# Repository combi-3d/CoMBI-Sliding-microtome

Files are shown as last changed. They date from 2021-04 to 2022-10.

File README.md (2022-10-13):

# CoMBI-S (sliding microtome) 

1. STL file for making a white attachment of paraffin block by 3D printer (Fig. 4, designed by Josephine Galipon and Hiroyoshi Shirahata). Choose filament color as you need as a background color. In our report, we made attachments in white, and also add white crayon into paraffin, to get better contrast between specimen and background.

2. Arduino sketch for CoMBI-S low-cost system (Suppl. Fig. S2, written by Tohru Murakami)

3. SVG file of frost distributor (Suppl. Fig. S3, designed by Yuki Tajika)
   Acrylic plate with desirable thickness (2 mm) are processed by CO2 laser cutter. 1. Engrave black lines, 2. Cut red lines. Then,  3. Bend at black lines using bending heater. Adjust the bending angle according to the shape of each blade holder.

4. SVG file of molds for embedding with white-agarose (Suppl. Fig. S4, designed by Yuki Tajika)
   Acrylic plate with desirable thickness (2, 3, 5-mm) are processed by CO2 laser cutter. 1. Engrave magenta lines, 2. Cut blue lines, 3. Cut black lines.
   Set the radius of one part to 40mm, or the size of all 8 parts to 158 x 81 mm. Make a countersink at the bottom of "bottom plate".

These are supplemental data in: Scientific Reports 2021; 11: 13108.

Published online 2021 Jun 23. doi: 10.1038/s41598-021-92485-5 under the CC BY 4.0 licence.

(2021.3 submitted, 2021.4 in revision, 2021.6 accepted. Scientific Reports)

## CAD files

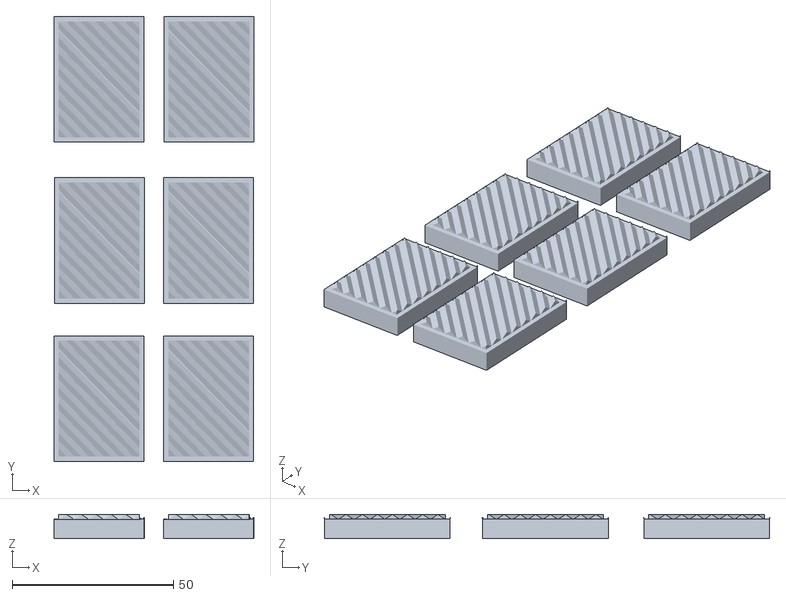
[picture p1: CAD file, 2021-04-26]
block 0001.stl
62.0 x 138.0 x 7.49

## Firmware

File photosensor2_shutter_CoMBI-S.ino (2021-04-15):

/*
  This sketch is used for CoMBI-S prototype system (low-cost type shown in Suppl.Fig S2).
  
  Arduino Uno R3 controls parts below:
  1. Photosensors (Omron, EE-SY310 or EE-SY410 detect the handle of the microtome.
  2. Optocouplers (Toshiba, TLP785GB) fix focus (half-push), and release shutter, when the handle passing above the sensors.
  3. DIP switch 1 selects photoreflector type (HIGH = Omron EE-SY310, LOW = Omron EE-SY310).
  4. DIP switch 2 selects the direction of the handle when the shutter is released (HIGH = going back(default), LOW = going forward).
  5. Push switches (alt, temp) are used to start serial imaging, or mamual camera control.
  6. LEDs indicate; executing serial imaging, detecting handle, fixing focus (half-push) and releasing shutter. 
 
  This work is licensed under a Creative Commons Attribution 4.0 International License.
  <http://creativecommons.org/licenses/by/4.0/>

  (c) 2016, Tohru Murakami, Gunma University.
*/

// Hardware constants. Adjust these values per installations.

const int latentcy = 100; // msec
const float baselineVoltage = 2.5; // threshold voltage of the photosensor; 0 – 5.0

// Pin assignments

// DIPSW Switch inputs

const int DIPSW_sensorTypeMismatch = 12;
const int DIPSW_sensorDirection = 13;

// Switch inputs
const int SWPin_autoControl = 3; // the auto-control switch
const int SWPin_contHalfPush = 4; // the continuous-half-push switch
const int SWPin_manualRelease = 5; // the manual-shutter-release switch

// Switch indicator outputs
const int ledPin_autoControl = 7; // the auto-control indicator
const int ledPin_contHalfPush = 6; // the continuous-half-push indicator

// Shutter indicator outputs
const int ledPin_halfPush = 8; // the half-push indicator
const int ledPin_release = 9; // the shutter-release indicator

// Shutter outputs
const int optoPin_halfPush = 11; // the half-push optocoupler
const int optoPin_release = 10; // the shutter-release optocoupler

// Sensor inputs (for default installation)
int sensorPin_halfPush = A1; // the half-push photosensor
int sensorPin_release = A0; // the shutter-release photosensor

// Serial communication rate

const int serialSpeed = 9600;

// Shutter status aliases

const int interval = 0;
const int standby = 1;

// DIPSW switch values (0 for default installation)

int sensorTypeMismatch = 0;
int sensorDirection = 0;

// Variables

int releaseCounter = 0; // count shutter release
int shutterStatus = interval;
int autoControl = 0;
int contHalfPush = 0;
int manualRelease = 0;
int sensorVal_halfPush; // 10 bit unsigned integer
int sensorVal_release; // 10 bit unsigned integer
float voltage_halfPush; // 0.0–5.0
float voltage_release; // 0.0–5.0

void setup() {

  int temp;

  // Assign output pins
  pinMode(optoPin_halfPush, OUTPUT);
  pinMode(optoPin_release, OUTPUT);
  pinMode(ledPin_autoControl, OUTPUT);
  pinMode(ledPin_contHalfPush, OUTPUT);
  pinMode(ledPin_halfPush, OUTPUT);
  pinMode(ledPin_release, OUTPUT);

  // Assign switche pins
  pinMode(DIPSW_sensorTypeMismatch, INPUT_PULLUP);
  // HIGH = light-ON sensor for dark signal or dark-ON for light signal; LOW = matched
  pinMode(DIPSW_sensorDirection, INPUT_PULLUP); //HIGH reverse; LOW default
  pinMode(SWPin_autoControl, INPUT_PULLUP); //HIGH automatic; LOW no shutter control
  pinMode(SWPin_contHalfPush, INPUT_PULLUP); //HIGH continuous half push; LOW sensor-controled half push
  pinMode(SWPin_manualRelease, INPUT_PULLUP); //HIGH shutter release

  // initialize output pins
  digitalWrite(ledPin_autoControl, LOW);
  digitalWrite(ledPin_contHalfPush, LOW);
  digitalWrite(optoPin_halfPush, LOW);
  digitalWrite(ledPin_halfPush, LOW);
  digitalWrite(optoPin_release, LOW);
  digitalWrite(ledPin_release, LOW);

  // read the DIP switches
  sensorTypeMismatch = digitalRead(DIPSW_sensorTypeMismatch); // HIGH = default, LOW = mismatch
  sensorDirection = digitalRead(DIPSW_sensorDirection);   // HIGH = default, LOW = reverse

  // adjust the sensor direction
  if (sensorDirection == LOW) {
    temp = sensorPin_halfPush; // Swap the sensor pin assignments
    sensorPin_halfPush = sensorPin_release;
    sensorPin_release = temp;
  }

  // initialize serial communication
  Serial.begin(serialSpeed);

  // print message when done.
  Serial.println("Photosensor-driven shutter controler ready!");
}

void loop() {

  // read the switches

  manualRelease = digitalRead(SWPin_manualRelease);
  autoControl = digitalRead(SWPin_autoControl);
  contHalfPush = digitalRead(SWPin_contHalfPush);

  if (manualRelease == LOW) { // releaes the shutter when the manual shutter release switch is pressed.

    Serial.print("Manual ");
    release();

  } else if (autoControl == LOW) {

    digitalWrite(ledPin_autoControl, HIGH);

    if (contHalfPush == LOW) { // leave the half-push HIGH when the continuous-half-push switch is ON

      digitalWrite(ledPin_contHalfPush, HIGH);
      digitalWrite(optoPin_halfPush, HIGH);

    } else if (shutterStatus == interval) {

      digitalWrite(ledPin_contHalfPush, LOW);
      digitalWrite(optoPin_halfPush, LOW);

    };

    // read the sensor values and convert them to voltage levels

    sensorVal_halfPush = analogRead(sensorPin_halfPush);
    sensorVal_release = analogRead(sensorPin_release);

    voltage_halfPush = (sensorVal_halfPush / 1024.0) * 5.0;
    voltage_release = (sensorVal_release / 1024.0) * 5.0;

    //     print the voltage levels on the serial port

    Serial.print("half push sensor: ");
    Serial.print(voltage_halfPush);
    Serial.print(", release sensor: ");
    Serial.println(voltage_release);

    if (sensorTypeMismatch == LOW) { // invert the sensor voltages when sensorTypeMismatch is bright ON

      voltage_halfPush = 5.0 - voltage_halfPush;
      voltage_release = 5.0 - voltage_release;

    };


    if (voltage_halfPush > baselineVoltage && voltage_release <= baselineVoltage && shutterStatus == interval) {
      // turn half-push HIGH when the half-push sensor detects something.

      digitalWrite(optoPin_halfPush, HIGH);
      digitalWrite(ledPin_halfPush, HIGH);

      shutterStatus = standby;

    };

    if (voltage_release > baselineVoltage && shutterStatus == standby) {
      // release the shutter when the release sensor detects something.

      release();

      shutterStatus = interval;

    };

  } else { // make everything zero when autoControl SW is off.

    Serial.println("OFF");
    digitalWrite(ledPin_autoControl, LOW);
    digitalWrite(ledPin_contHalfPush, LOW);
    digitalWrite(optoPin_halfPush, LOW);
    digitalWrite(ledPin_halfPush, LOW);
    digitalWrite(optoPin_release, LOW);
    digitalWrite(ledPin_release, LOW);

    shutterStatus = interval;

  };
}

void release() {

  digitalWrite(optoPin_halfPush, HIGH);
  digitalWrite(ledPin_halfPush, HIGH);

  delay(latentcy); // give the optocoupler a moment to activate

  digitalWrite(optoPin_release, HIGH);
  digitalWrite(ledPin_release, HIGH);

  delay(latentcy); // give the optocoupler a moment to activate

  digitalWrite(optoPin_release, LOW);
  digitalWrite(ledPin_release, LOW);
  digitalWrite(ledPin_halfPush, LOW);

  if (contHalfPush != LOW) {

    digitalWrite(optoPin_halfPush, LOW);

  };

  Serial.print("# ");
  Serial.println(releaseCounter++);

}
